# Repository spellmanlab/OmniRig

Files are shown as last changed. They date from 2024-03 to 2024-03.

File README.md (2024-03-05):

OmniRig is a versatile platform for head-fixed rodent experiments. The repository includes everything you'll need to get started:
1. 3D printable STL files
2. A printable circuit board design
3. A comprehensive parts list, complete with sources and prices
4. Arduino scripts for testing the rig and running behavioral experiments
5. A training protocol for habituation and training

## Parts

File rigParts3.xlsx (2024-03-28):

component | item description | # / rig | usage notes | part ID | supplier | link
base + head restraint | 6"x6" breadboard | 1 |  | MB6 | Thorlabs | https://www.thorlabs.com/thorproduct.cfm?partnumber=MB6
 | 3" x 1/2" posts | 2 | supports head plates | TR3 | Thorlabs | https://www.thorlabs.com/thorproduct.cfm?partnumber=TR3
 | adhesive teflon sheet, Teflon (PTFE) sheets, various sizes, 0.03" (1/32") thick, with 3M 300LSE industrial-strength self-adhesive backing [TEFLON-3M-all] | 1 | covers the base, makes for easier cleanup | 3M | 3M | https://www.amazon.com/Teflon-industrial-strength-self-adhesive-backing-TEFLON12x12-3M/dp/B00CM06JAG
 | Adapter with Internal 4-40 Threads and External 1/4"-20 Threads | 2 | mounting arduino to base | AE4E25E | Thorlabs | https://www.thorlabs.com/thorproduct.cfm?partnumber=AE4E25E#ad-image-0
air/water control | flowmeter, Masterflex Variable-Area Flowmeter with Valve, Acrylic Housing, Brass Fitting, 50-mm; 0.5 LPM Air | 1 | regulates airflow to odorants | 2968K201 | McMaster-Carr | https://www.mcmaster.com/2968K201/
 | M5 screw | 1 | secures flow meter to holder
 | Luer 3-way stopcock, F/F/M | 2 | air and water intake |  | generic | https://www.amazon.com/MEETOOT-Disposable-Stopcocks-Connections-Experimental/dp/B0BWJ7N44D?s=industrial
 | Luer 3-way T splitter, F/F/M | 5 | coupled to water and odorant bottles |  | generic
 | Luer 3/32" barbed connector, F | 1 | connects water bottle to water intake stopcock |  | generic
 | Luer 3/32" barbed connector, M | 10 | 1) connects air intake to flowmeter, 2) connects water intake to water solenoids, 3-10) connect odorant bottles to intake and exhaust tubes | 67156 | US Plastic Corp | https://www.usplastic.com/catalog/item.aspx?itemid=118335&clickid=search
 | Luer elbow adaptor, M-F | 3 | 1) connects water bottle to water intake, 2-3) couple to lickspout needles |  | generic
 | Luer snap-on threads | 8 | secure male luer adapters to female luer adapters |  | generic
 | 6-40 threaded ferrules | 24 | coupling to for 1/16" OD tubing | SKU 640FF-16 | Globalfia | https://www.globalfia.com/shop/6-40-Fittings-p460224016
 | 1/4 OZ luer-capped dispensing bottles | 4 | contains odorants | JG0.25BC | Test Equity | https://www.testequity.com/category/Electronic-Production-Supplies/Bottles-And-Dispensers/Bottles/167SO020-JG2-0BC
 | 1 OZ luer-capped dispensing bottle | 1 | contains water | JG2.0BC Bl2 | Test Equity | https://www.usplastic.com/catalog/item.aspx?itemid=117424
 | NPT barb (1/8" or 3/32") | 2 | connecting 1/16" PTFE tubing to flowmeter intake and exhaust | 64297 | US Plastic Corp | https://www.usplastic.com/catalog/item.aspx?itemid=33656
 | TUBING
lick stage | gavage needle, 18g | 2 |  |  | GavageNeedle | https://gavageneedle.com/products/reusable-oral-gavage-needle?variant=865840675
 | translating post | 1 | hold lick ports | BTP2.0 (https://www.newport.com/p/BTP2.0) | Newport | https://www.newport.com/f/0.5-in.-translating-optical-posts
 | xy translating stage | 1 | hold lick ports | M-MT-XY | Newport | https://www.newport.com/p/M-MT-XY
 | 6-40 machine nut | 2 | hold odorant tube
 | MINSTAC 6-40 threaded ferrule for 1/16" OD tubing | 1 | hold odorant tube
 | gasket washers | 1 |  | Hilitchi 270-Pcs #6#8#10#12 Stainless Steel Neoprene EPDM Bonded Sealing Gasket Washers Assortment Kit | Amazon (Hilitchi) | https://www.amazon.com/Hilitchi-270-Pcs-Stainless-Neoprene-Assortment/dp/B07DK91QBP
 | plastic 8/32" thumb screw | 1
mouse stage | toy tank treads | 76 links |  | treadmill belt | Amazon | https://www.amazon.com/Assembled-Workable-T-34-76-T-34-85-Self-propelled/dp/B07Q9QJSNC
 | steel bearings | 6 | treadmill axle bearings | F686ZZ | Amazon | https://www.amazon.com/dp/B07Z38H4JB?s=industrial&sp_csd=d2lkZ2V0TmFtZT1zcF9kZXRhaWw
 | 2" mini posts | 3 | treadmill axles | MS2R | Thorlabs | https://www.thorlabs.com/thorproduct.cfm?partnumber=MS2R
 | 4-40 screws and washers | 1 |  |  | Fastener Express | http://www.fastener-express.com/browseproducts/4-40-Alloy-Assortment-click-for-details..html
 | rotary encoder | 1 | measure running speed | AMT103-V | Digi-key | https://www.digikey.com/en/products/detail/cui-devices/AMT103-V/827016?s=N4IgTCBcDaIIIFkAqBGADAZgLQDUQF0BfIA
 | low-profile 1/4-20 cap screws | 4 | secure treadmill to breadboard | 1AYL9 | Grainger
 | 8/32" screws and nuts | 2 | secure walls
command stage | 2-way solenoid valves, 12v, face-mounted | 2 | solenoid valves for dispensing water reward | LHDB1252115H | The Lee Company | https://www.theleeco.com/resources/files/2-port-hdi-solenoid-valve-pds-124-2014-12/
 | 3-way solenoid valves, 12v, face-mounted | 4 | route air to one of the four odorant tubes or bypass all four | LHDA1221411H | The Lee Company | https://www.theleeco.com/products/electro-fluidic-systems/solenoid-valves/control-valves/lhd-series/3-port/face-mount/
 | face-mounted 3-way manifold, 3-port | 1 |  | LFMX0510513B | The Lee Company | https://www.theleeco.com/products/electro-fluidic-systems/solenoid-valves/control-valves/standard-3-port-face-mount-style-manifolds/
 | face-mounted 3-way manifold, 1-port | 1 |  | LFMX0507200A | The Lee Company | https://www.theleeco.com/products/electro-fluidic-systems/solenoid-valves/control-valves/standard-3-port-face-mount-style-manifolds/
 | face-mounted 2-way manifold, 3-port | 1 |  | LFMX0527450B | The Lee Company | https://www.theleeco.com/products/electro-fluidic-systems/solenoid-valves/control-valves/standard-2-port-face-mount-style-manifolds/
 | retention brackets | 3 | attaches selonoids to face mount manifolds | LLWX0307130A | The Lee Company | https://www.theleeco.com/products/electro-fluidic-systems/solenoid-valves/control-valves/general-accessories-replacement-parts/
 | Arduino Mega 2560 | 1 | controls behavior |  | Amazon | https://www.amazon.com/ARDUINO-MEGA-2560-REV3-A000067/dp/B0046AMGW0
 | SmartWAV Arduino-compatible sound board |  |  | (legacy model) | Vizic Technologies | https://www.vizictechnologies.com/product-page/smartwav-audio-processor
 | Custom arduino shield (see schematic, SSShield6) | 1 | translates Arduino commands into actuator logic
 | H-bridge | 2 | multiplexed transistor | SN754410 | Sparkfun.com | https://www.sparkfun.com/products/315
 | 6-pin screw terminal, 2.54mm pitch | 2 | connecting wires to board | PRT-16499 | Sparkfun.com | https://www.sparkfun.com/products/16499
 | 8-pin stackable female header | 2 | connecting wires to board and board to arduino | PRT-09279 | Sparkfun.com | https://www.sparkfun.com/products/9279
 | 2-pin stackable female header | 7 | connecting solenoids to board |  | Phoenix Enterprizes | https://www.peconnectors.com/female-headers-pcb-1x-row-.100/hws15768/?vt_keyword=
 | 6-pin female header | 2 | connecting sound board to main board |  | Phoenix Enterprizes | https://www.peconnectors.com/female-headers-pcb-1x-row-.100/hws1068/
 | 6-pin male header | 2 | connecting board to arduino |  | Phoenix Enterprizes | https://www.peconnectors.com/pin-headers-straight-1x-row-.100/hws2382/?vt_keyword=
 | 1MOhm resistors | 11 | Dropping current |  | Amaon | https://www.amazon.com/Projects-Resistors-Watt-Choose-Quantity/dp/B00CVZ4T7W?th=1
general
 | Luer stopcock kit | 1 |  | 72-1664 | Harvard Apparatus | https://www.harvardapparatus.com/luer-stopcock-kit-1.html
 | Male Luer taper connection kit, natural polypropylene | 1 |  | 72-2739 | Harvard Apparatus | https://www.harvardapparatus.com/luer-to-tube-connector-kits.html
 | Luer connection kit, natural polypropylene | 1 |  | 72-1407 | Harvard Apparatus | https://www.harvardapparatus.com/luer-to-tube-connector-kits.html
 | Masterflex L/S® Precision Pump Tubing, Peroxide-Cured Silicone, L/S 13; 1/32" ID, 25 ft | 25ft | enables tight sealing at connection points with the 1/16" OD PTFE tubing, which is used for most air and water flow in the rig | ED-96400-13 | Cole-Parmer | https://www.coleparmer.com/i/masterflex-l-s-peroxide-cured-silicone-tubing-l-s-13-25-ft/9640013?PubID=ZM&persist=True&ip=no
 | Silicone (peroxide-cured) Tubing, 1/16"id X 1/8"OD, 25 Ft/pack | 25ft | carries air from flowmeter to air valves and between valves | EW-06411-62 | Cole-Parmer | https://www.coleparmer.com/i/masterflex-transfer-tubing-peroxide-cured-silicone-1-16-id-x-1-8-od-25-ft/0641162?searchterm=EW-06411-62
 | Masterflex Transfer Tubing, PTFE, 1/32" ID x 1/16 " OD; 25 ft |  | carries air and water through most connections in the rig | EW-06407-41 | Cole-Parmer | https://www.coleparmer.com/i/masterflex-transfer-tubing-ptfe-1-32-id-x-1-16-od-25-ft/0640741?searchterm=06407-41
 | Polyethylene tubing | 25ft | connects 1/16" OD PTFE tubing to barbed connectors |  | Amazon | https://www.amazon.com/USA-Sealing-Polyethylene-Tubing-Long/dp/B0853CTJXX
 | 1/4-20 machine screw kit | 1 | secures component holders to breadboard | HW-KIT2 | Thorlabs | https://www.thorlabs.com/thorproduct.cfm?partnumber=HW-KIT2
 | 8-32 machine screw kit | 1 | secures component holders to breadboard | HW-KIT3 | Thorlabs | https://www.thorlabs.com/thorproduct.cfm?partnumber=HW-KIT3
 | 1/16" OD PTFE tubing cuts: | 8" (4x) | odorant tubes to manifold, outflow luer valve one side, 6-40 ferrule on the other
 |  | 10" (4x) | solenoids to odorant tubes, inflow luer valve one side, 6-40 ferrule on the other
 |  | 7" (1x) | clean air solenoid to manifold, 6-40 ferrules both sides
 |  | 1" (3x) | solenoid-to-solenoid, 6-40 ferrules both sides
 |  | 12" (1x) | water, stopcock to solenoid, 6-40 ferrule one side, male luer barb on the other
 |  | 6" (2x) | water, solenoids to lick spouts, 6-40 ferrule one side, male luer bard on the other
 |  | 12" (1x) | water bottle to stopcock, female luer barb one side, other side bare
 |  | 4" (1x) | air stopcock to flow regulator, NPT barb one side, male luer barb on the other
 |  | 12" (1x) | flow regulator to solenoid, NPT barb one side, 6-40 ferrule on the other

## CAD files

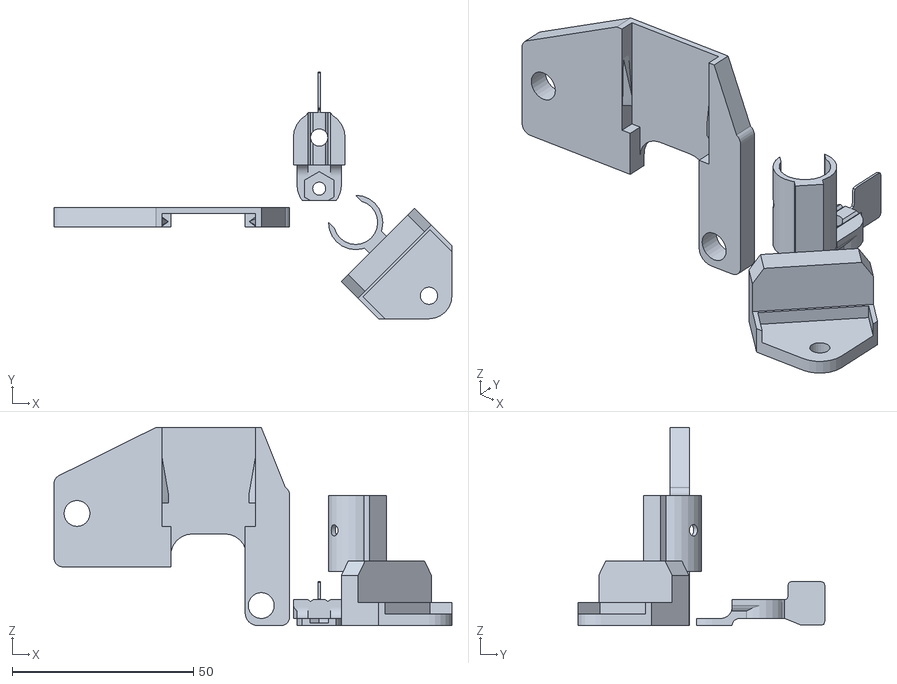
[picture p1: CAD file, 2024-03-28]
lickSpoutPostHolder_Multi.stl
109.7 x 68.0 x 54.7

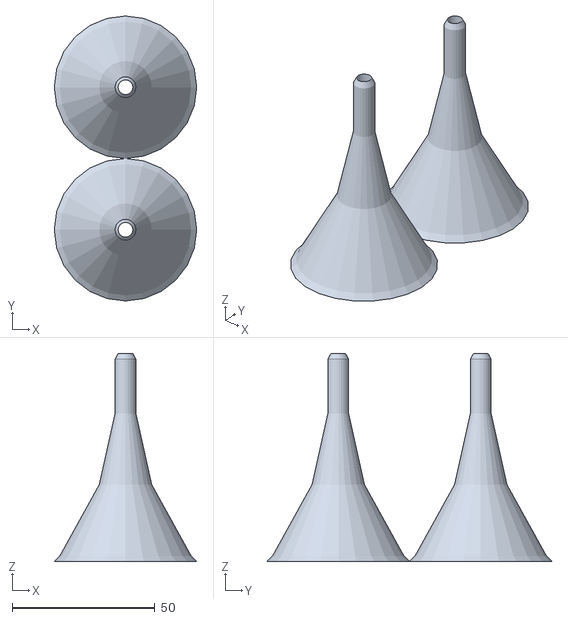
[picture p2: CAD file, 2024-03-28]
speakerfunnel.stl
50.0 x 100.0 x 73.0

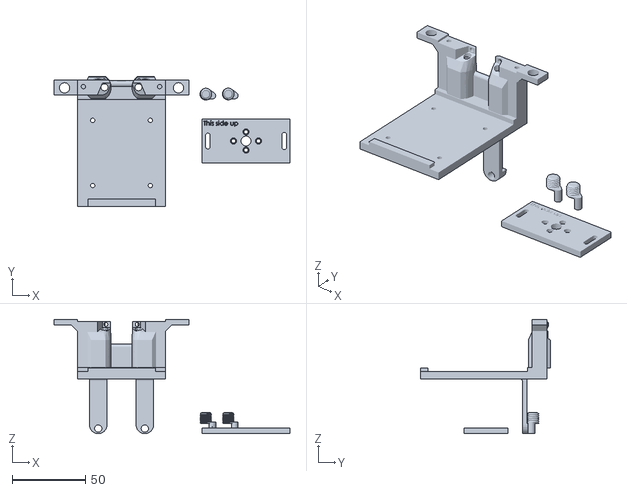
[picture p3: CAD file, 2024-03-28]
SIR_Headport13.stl
160.9 x 88.7 x 78.0

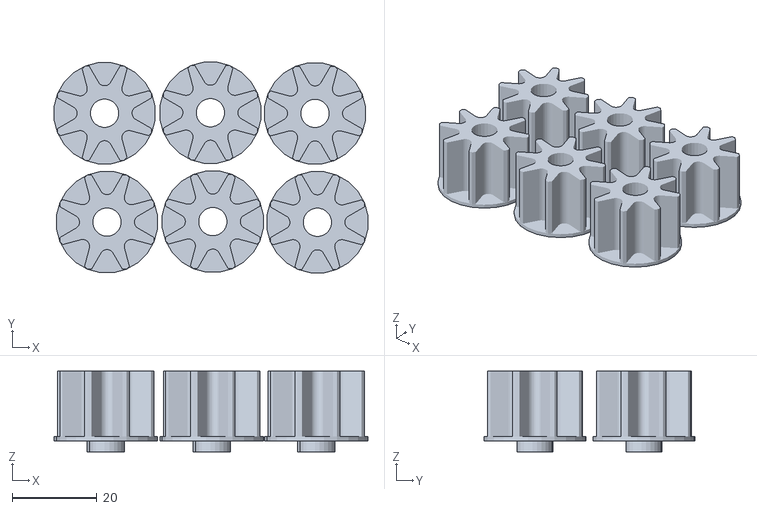
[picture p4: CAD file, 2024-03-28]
treadmillSprockets.stl
74.3 x 49.9 x 19.1

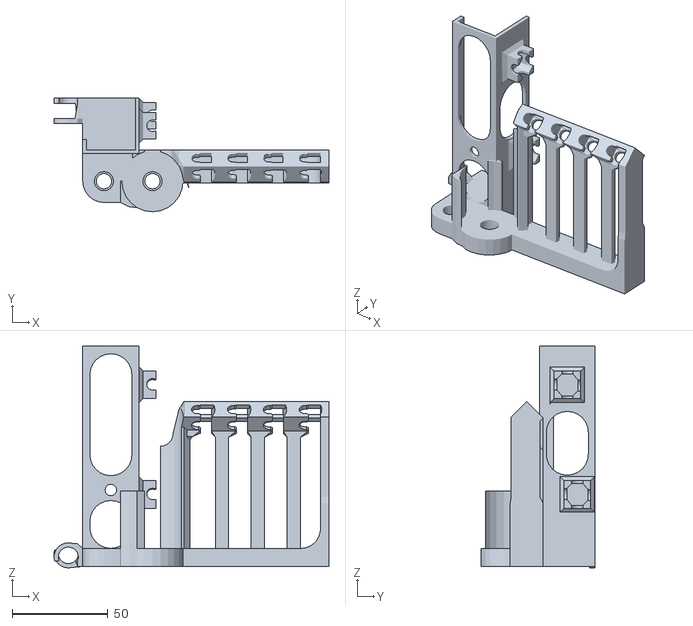
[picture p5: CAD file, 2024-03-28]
airWaterHolder.stl
143.8 x 59.4 x 116.0

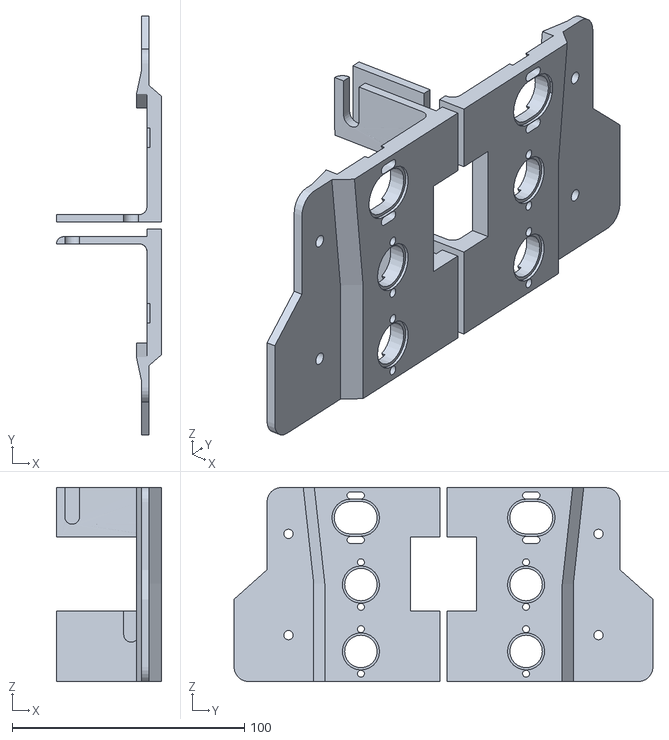
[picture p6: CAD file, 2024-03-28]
treadmillBase.stl
45.4 x 180.6 x 83.7

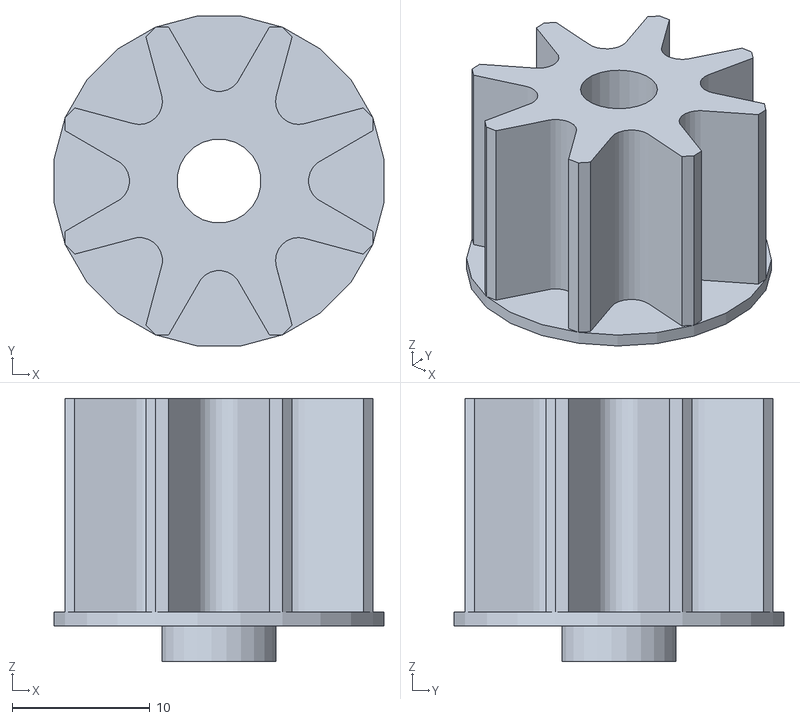
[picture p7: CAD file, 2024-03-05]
treadmillSprocket3_fixed.stl
23.9 x 23.9 x 19.1

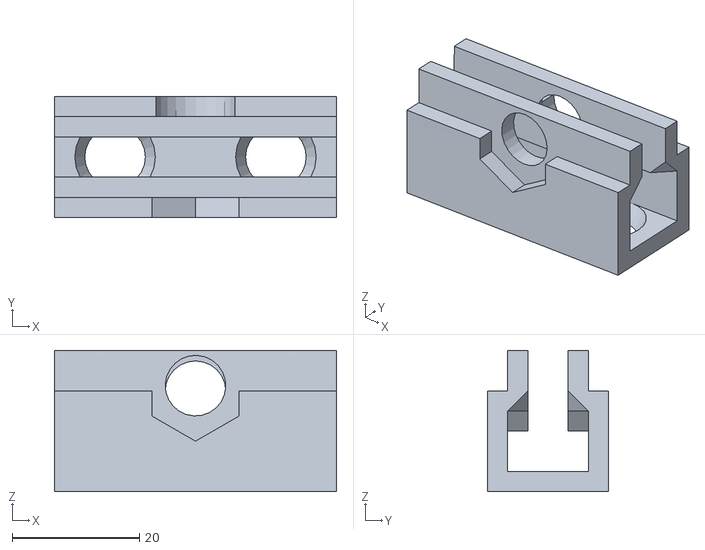
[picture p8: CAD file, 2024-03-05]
floorClamp.stl
44.3 x 19.0 x 22.2

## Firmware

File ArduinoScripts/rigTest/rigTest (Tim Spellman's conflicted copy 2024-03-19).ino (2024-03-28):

#include <SPI.h>
#include <TrueRandom.h>
#include <elapsedMillis.h>
#include <Average.h>
elapsedMillis timeElapsed;

#include <DFRobot_DF1201S.h>
DFRobot_DF1201S DF1201S;
int H2OL = 7;
int H2OR = 6;
int odorAirSupply = 5;
int odorPair = 10;
int odorAB = 11;  //LOW=A;HIGH=B
int odorCD = 8;   //LOW=C;HIGH=D
int optoChan = 38;
int whiskerVolumes[] = { 5, 10, 25, 50 };
int waiting = 1;                        //used in while-loops
int session = 0;
int runLoop = 1;

void setup() {
  Serial1.begin(115200);
  while (!DF1201S.begin(Serial1)) {
    Serial.println("Init failed, please check the wire connection!");
    delay(1000);
  }
  DF1201S.setPrompt(false);
  DF1201S.setLED(false);
  DF1201S.setVol(/*VOL = */ 20);          //Sets audio card volume 20 max.
  DF1201S.switchFunction(DF1201S.MUSIC);  //This command makes the speakers say "Music"
  DF1201S.setPlayMode(DF1201S.SINGLE);    //Makes it so the player will stop if it reaches the end of a file
                                          //END NEW

  pinMode(3, OUTPUT);
  pinMode(2, INPUT);
  pinMode(9, OUTPUT);
  Serial.begin(9600);
  pinMode(H2OL, OUTPUT);
  pinMode(H2OR, OUTPUT);
  pinMode(odorAirSupply, OUTPUT);
  pinMode(odorPair, OUTPUT);
  pinMode(odorAB, OUTPUT);  //Low=A,High=B;
  pinMode(odorCD, OUTPUT);  //Low=C,High=D;
  pinMode(8, OUTPUT);
  pinMode(12, OUTPUT);
  pinMode(13, OUTPUT);
  pinMode(38, OUTPUT);
  pinMode(39, OUTPUT);
  pinMode(40, OUTPUT);
  pinMode(41, OUTPUT);
  pinMode(42, OUTPUT);
  pinMode(43, OUTPUT);
  pinMode(44, OUTPUT);
  pinMode(45, OUTPUT);
  pinMode(46, OUTPUT);
  pinMode(47, OUTPUT);
  pinMode(48, OUTPUT);
  pinMode(49, OUTPUT);
  pinMode(50, OUTPUT);
  pinMode(51, OUTPUT);
  pinMode(52, OUTPUT);
  pinMode(53, OUTPUT);
  digitalWrite(H2OL, LOW);
  digitalWrite(H2OR, LOW);
  digitalWrite(9, LOW);
  digitalWrite(odorAirSupply, LOW);
  digitalWrite(odorPair, LOW);
  digitalWrite(odorAB, LOW);
  digitalWrite(odorCD, LOW);
  digitalWrite(12, LOW);
  digitalWrite(13, LOW);
  digitalWrite(38, LOW);
  digitalWrite(40, LOW);
  digitalWrite(41, LOW);
  digitalWrite(42, LOW);
  digitalWrite(43, LOW);
  digitalWrite(44, LOW);
  digitalWrite(45, LOW);
  digitalWrite(46, LOW);
  digitalWrite(47, LOW);
  digitalWrite(48, LOW);
  digitalWrite(49, LOW);
  digitalWrite(50, LOW);
  digitalWrite(51, LOW);
  digitalWrite(52, LOW);
  digitalWrite(53, LOW);
  timeElapsed = 0;
  randomSeed(analogRead(0));


  Serial.println("How many test loops?");
  while (waiting == 1) {
    if (Serial.available() > 0) {   // is a character available?
      runLoop = Serial.parseInt();  // get the character
      if (runLoop > 0) {
        waiting = 0;
      }
    }
  }
  waiting=1;

  Serial.println("Choose action:");
  Serial.println("(1) Test Water Lines");
  Serial.println("(2) Play Tones");
  Serial.println("(3) Test Odorant Lines");
  Serial.println("(4) Test Lick Detectors");
  Serial.println("(5) Opto Pulses");

}

void loop() {

  while (waiting == 1) {
    if (Serial.available() > 0) {   // is a character available?
      session = Serial.parseInt();  // get the character
      if (session > 0) {
        waiting = 0;
      }
    }
  }
  waiting=1;

  if (session == 1) {
    //TEST WATER SPOUTS
    for (int i=1; i<=runLoop; i++){
      delay(100);
        Serial.println("Testing left water spout");
      digitalWrite(H2OL, HIGH);
      delay(35);
      digitalWrite(H2OL, LOW);
      delay(1000);
      Serial.println("Testing right water spout");
      digitalWrite(H2OR, HIGH);
      delay(35);
      digitalWrite(H2OR, LOW);
      delay(1000);
    }
  }

  else if (session == 2) {
    Serial.println("Testing tones");
    for (int i=1; i<=runLoop; i++){
    // TEST TONES//
      delay(1000);
      DF1201S.playFileNum(17);
      DF1201S.setPlayTime(/*Play Time = */ 0);
      delay(500);
      DF1201S.setPlayTime(/*Play Time = */ 4);
      delay(1000);
  
      DF1201S.playFileNum(19);
      DF1201S.setPlayTime(/*Play Time = */ 0);
      delay(500);
      DF1201S.setPlayTime(/*Play Time = */ 4);

    }    
  } 
  
    else if (session == 3) {
    Serial.println("Testing odorant lines");
    for (int i=1; i<=runLoop; i++){
      ////// TEST ODORANT LINES //
      digitalWrite(odorAirSupply, HIGH);
      digitalWrite(odorPair, LOW);
      digitalWrite(odorAB, LOW);
      delay(2000);
      digitalWrite(odorAB, HIGH);
      delay(1000);
      digitalWrite(odorAB, LOW);
      digitalWrite(odorPair, HIGH);
      digitalWrite(odorCD, LOW);
      delay(1000);
      digitalWrite(odorCD, HIGH);
      delay(1000);
      digitalWrite(odorAirSupply, LOW);
      digitalWrite(odorPair, LOW);
      digitalWrite(odorAB, LOW);
      digitalWrite(odorCD, LOW);
      delay(2000);
    }
  }

  else if (session == 4) {
    timeElapsed = 0;
    Serial.println("Testing lick detectors!");
    while(timeElapsed < 10000){
    //// TEST LICK DETECTORS //
    Serial.println(analogRead(A0) - analogRead(A5));
    delay(10);
    }
      Serial.println("Choose action:");
      Serial.println("(1) Test Water Lines");
      Serial.println("(2) Play Tones");
      Serial.println("(3) Test Odorant Lines");
      Serial.println("(4) Test Lick Detectors");
      Serial.println("(5) Opto Pulses");
  }

  else if (session == 5) {
    Serial.println("Testing Opto Pulses!");
    for (int i=1; i<=runLoop; i++){
      ///// TEST OPTO PULSES //////
      digitalWrite(46,HIGH);
      digitalWrite(optoChan, HIGH);
      delay(100);
      digitalWrite(optoChan, LOW);
      digitalWrite(46,LOW);
      delay(4000);
    }
  }


  delay(1000);

}

;

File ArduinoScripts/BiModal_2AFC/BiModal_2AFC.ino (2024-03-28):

//INCLUDE RELEVANT LIBRARIES
#include <SPI.h>
#include <TrueRandom.h>
#include <elapsedMillis.h>
#include <Average.h>
#include <DFRobot_DF1201S.h>
elapsedMillis timeElapsed;
DFRobot_DF1201S DF1201S;


//SET SESSION-SPECIFIC PARAMETERS
float prop = 10;                //sets proportion of trials that are incongruent (this number over 20)
float critScore = 0.8;          //sets criterion score needed to change blocks, set >1 to never reach
int delayTime = 15;             //open time on water solenoid, in ms (~15ms for 3psi)
int LBCorrect = 1;              //actively correct for side bias? 1=Y; 0=N;
int trialStartTone=18;          
int whiteNoiseRight=19;
int whiteNoiseLeft=17;
int tone1=9; 
int tone2=7;


//INITIALIZE SESSION-SPECIFIC PLACEHOLDER VARIABLES
int session;                    //index within the corresponding sessionNames array
String sessionNames[] =  {"Simple Discrimination", "Compound Discrimination", "Intradimensional Shift", "Reversal", "Extradimensional shift", "Intradimensional shift B" , "Serial Extradimensional Shifts"};
int lightStimYN;                //whether to deliver optogenetic stimuli, 1 = No; 2 = Yes
int keyDetect;                  //will be used to input data at session outset
int A;                          //will be used to input data at session outset
int seqNum = 0;                 //set to 0 to start from beginning of set sequence in setChoose
int setChoose [] = {1, -1};     //assign set -- 1 for whisker, -1 for odor
int blockMax = 1;               //maximum number of blocks (sets) in a session
int mapID = 1;                  //used to reverse the left-right stimulus mapping on and after the Reversal session
int odorID = 1;                 //0=A,1=B
int toneID = 1;
int trialMax = 350;                     //maximum length of a session
int toneDur = 500;                      //duration of trial initiation tone
int volMax = 100;                        //sound card output volume (max 255)
int trialChoose [] = { -1, -1, -1, -1, -1, -1, 1, 1, 1, 1, 1, 1};  //used to select left/right (-1/1) reward location for each trial
int irrelChoose [] = {1, 1, 1, 1, 1, 1, 1, 1, 1, 1, 1, 1, 1, 1, 1, 1, 1, 1, 1, 1 }; // choose irrelevant stim -- -1 for incongruent, 1 for congruent
int crit = 0;                           //criterion reached (1) or not (0)
float lickThresh = 20;                  //threshold voltage difference for lick detection
int lickPrev = 0;                       //whether the mouse has already licked within a given time window
int waiting = 1;                        //used in while-loops
int brightness = 250;                   //for overhead light
int fadeAmount = 5;                     //for overhead light


//INITIALIZE TRIAL VARIABLES
int toneLR;
int odorLR;
int blockNum = 0;
int setID;
int trialLR;
int stimLR;
int irrelLR;
int blockTrial;


//ASSIGN VARIABLES TO ARDUINO PINS
int LEDChannel = 40;
int optoChannel = 38;
int H2OL = 7;
int H2OR = 6;
int odorAirSupply = 5;
int odorPair = 10;
int odorAB = 11;
int odorCD = 8;
int currO = odorAB;
int setIDOut = 52;
int trialOut = 53;
int trialLROut = 50;
int irrelLROut = 51;
int lickingLOut = 48;
int lickingROut = 49;
int rewardOut = 46;


//INITIALIZE PERFORMANCE VARIABLES
Average<float> runAveNG(10);    //initialize a moving window for tracking motivation
Average<float> lickAveR(3);     //initialize a moving window for detecting right licks
Average<float> lickAveL(3);     //initialize a moving window for detecting left licks
Average<float> lickBias(10);    //initialize a moving window for tracking side bias
Average<float> runAveL(10);     //initialize a moving window for tracking left trial accuracy
Average<float> runAveR(10);     //initialize a moving window for tracking right trial accuracy
Average<float> runAve(30);      //initialize a moving window for tracking overall accuracy
int RT = 0;
int ITI = 0;
int trial = 0;
int lickedR = 0;
int lickedL = 0;
int lickNumR = 0;
int lickNumL = 0;
int trialCorrect = 0;
int totalDispensed = 0;
int response = 0;


//SETUP SECTION
void setup() {
  Serial.begin(9600);
  pinMode(LEDChannel, OUTPUT); digitalWrite(LEDChannel, HIGH);
  pinMode(optoChannel, OUTPUT); digitalWrite(LEDChannel, LOW);
  pinMode(12, OUTPUT); digitalWrite(12, LOW);
  pinMode(3, OUTPUT);
  pinMode(9, OUTPUT); digitalWrite(9, LOW);
  pinMode(H2OL, OUTPUT);
  pinMode(H2OR, OUTPUT);


//START AUDIO
  Serial1.begin(115200);
  while(!DF1201S.begin(Serial1)){
    Serial.println("Init failed, please check the wire connection!");
    delay(1000);
  }
  DF1201S.setPrompt(false);
  DF1201S.setLED(false);
  DF1201S.setVol(/*VOL = */14); //Sets audio card volume 20 max. 
  DF1201S.switchFunction(DF1201S.MUSIC); //This command makes the speakers say "Music"
  DF1201S.setPlayMode(DF1201S.SINGLE); //Makes it so the player will stop if it reaches the end of a file

  analogWrite(LEDChannel, brightness);
  pinMode(odorAirSupply, OUTPUT); digitalWrite(odorAirSupply, LOW);
  pinMode(odorPair, OUTPUT); digitalWrite(odorPair, LOW);
  pinMode(odorAB, OUTPUT); digitalWrite(odorAB, LOW); //Low=A,High=B;
  pinMode(odorCD, OUTPUT); digitalWrite(odorCD, LOW); //Low=C,High=D;
  digitalWrite(H2OL, LOW);
  digitalWrite(H2OR, LOW);
  pinMode(setIDOut, OUTPUT); digitalWrite(setIDOut, LOW);
  pinMode(trialOut, OUTPUT); digitalWrite(trialOut, LOW);
  pinMode(trialLROut, OUTPUT); digitalWrite(trialLROut, LOW);
  pinMode(irrelLROut, OUTPUT); digitalWrite(irrelLROut, LOW);
  pinMode(lickingLOut, OUTPUT); digitalWrite(lickingLOut, LOW);
  pinMode(lickingROut, OUTPUT); digitalWrite(lickingROut, LOW);
  pinMode(rewardOut, OUTPUT); digitalWrite(rewardOut, LOW);
  digitalWrite(H2OL, HIGH);
  delay(delayTime);
  digitalWrite(H2OL, LOW);
  digitalWrite(H2OR, HIGH);
  delay(delayTime);
  digitalWrite(H2OR, LOW);
  randomSeed(analogRead(0));
  for (int q = 0; q < 10; q++) {
    runAveNG.push(1);
  }


  //CHOOSE SESSION
  delay(500);
  waiting = 1;
  Serial.println("");
  Serial.println("Choose session:");
  Serial.println("(0) SD"); Serial.println("(1) CD"); Serial.println("(2) IDS"); Serial.println("(3) Rev"); Serial.println("(4) EDS"); Serial.println("(5) IDSB"); Serial.println("(6) SEDS");
  while (waiting == 1) {
    if (Serial.available() > 0) {    // is a character available?
      session = Serial.parseInt();       // get the character
      if (session >= 0 && session <= 6) {
        waiting = 0;
      }
    }
  }

  delay(500);
  waiting = 1;
  Serial.println("");
  Serial.println("Opto stimulation during ITI ?");
  Serial.println("(1) No"); Serial.println("(2) Yes");
  while (waiting == 1) {
    if (Serial.available() > 0) {    // is a character available?
      lightStimYN = Serial.parseInt();       // get the character
      if (lightStimYN == 1 || lightStimYN == 2) {
        waiting = 0;
      }
    }
  }

  //SET SESSION-SPECIFIC PARAMETERS
  if (session >= 2) {         //ID shift, new whisker stimuli
    tone1=4;
    tone2=6;
  }
  if (session >= 3) {
    mapID = -1;               //Reversal and all sessions after
  }
  if (session >= 4) {
    seqNum = 1;               //ED shift 1
  }
  if (session >= 5) {
    currO = odorCD;           //switch odorants
  }
  if (session < 6) {          // set icg/cg proportion
    for (int i = 0; i < 11; i++) {
      irrelChoose[i] =  irrelChoose[i] * (-1);
    }
  }
  else {                      //for SEDS sessions
    for (int i = 0; i < prop; i++) {
      irrelChoose[i] = irrelChoose[i] * (-1);
    }
    blockMax = 20;
    seqNum = 0;               //start with whisker
    trialMax = 1000;
  }
  Serial.print("Begin Session ");
  Serial.println(sessionNames[session]);
  Serial.println("Press any key to begin");
  Serial.println("");
  A = 1;
  while (Serial.available() > 0) {
    Serial.read();
  }
  while (A == 1) {
    if (Serial.available()) {    // is a character available?
      waiting = 0;
      A = 0;
    }
  }

  digitalWrite(odorAirSupply, LOW);
  digitalWrite(odorPair, LOW);
  digitalWrite(odorAB, LOW); //Low=A,High=B;
  digitalWrite(odorCD, LOW);
  Serial.println("");
  Serial.print("n"); Serial.print("\t");
  Serial.print("blknum"); Serial.print("\t");
  Serial.print("iti"); Serial.print("\t");
  Serial.print("setID"); Serial.print("\t");
  Serial.print("trial"); Serial.print("\t");
  Serial.print("stim"); Serial.print("\t");
  Serial.print("irrelLR"); Serial.print("\t");
  Serial.print("lnL"); Serial.print("\t");
  Serial.print("lnR"); Serial.print("\t");
  Serial.print("rt"); Serial.print("\t");
  Serial.print("resp"); Serial.print("\t");
  Serial.print("corr"); Serial.print("\t");
  Serial.print("rAL"); Serial.print("\t");
  Serial.print("rAR"); Serial.print("\t");
  Serial.print("rANG"); Serial.print("\t");
  Serial.print("rA"); Serial.print("\t");
  Serial.print("H2O"); Serial.print("\t");
  delay(3000);
  timeElapsed = 0;
}
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
